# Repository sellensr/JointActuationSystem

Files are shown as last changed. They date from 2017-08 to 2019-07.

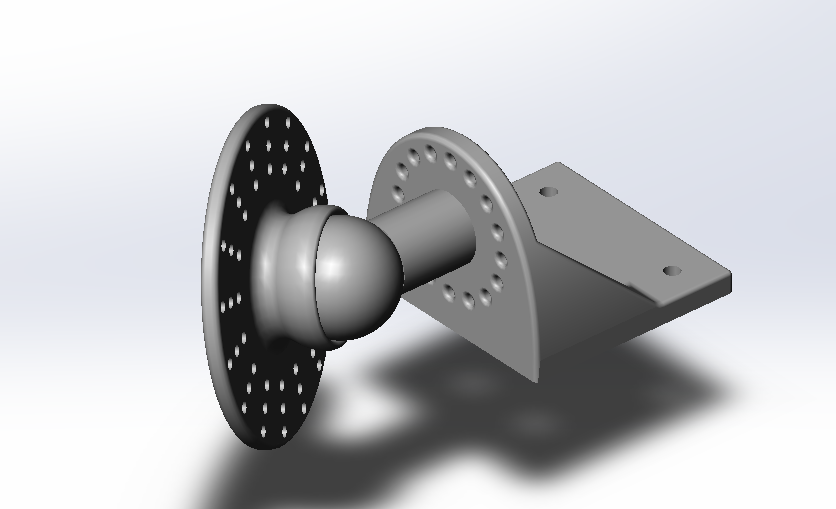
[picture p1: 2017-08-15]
Part Designs/CTP/CTP Assembly.png

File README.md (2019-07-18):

# JointActuationSystem
Details of the design of an Actuation System for wrist motion simulation as detailed in the master's thesis by Matthew Pearson titled: An Open-Source Device for Tendon Actuated Wrist Motion. 

Further details on the design, manufacture and testing are presented in the thesis found in this repository or [THESIS LINK]

Code original to the thesis is left intact in /Code/AP Source Code and /Code/Aurora AMP Source Code. Current development is taking place in /Code/MP-Sim_AP and Qualisys_AMP

## Generalization for other joints

Original coordinates and angle naming (only two angles, flexion-extension and radial-ulnar) were specific to a system of 4 actuators and the wrist joint. Additions to the /Code structure generalize to 3 x-y-z angles within a right hand coordinate system with y positive distally and z positive vertically upwards. Rotation about the x axis thus corresponds to flexion-extension and rotation about the z axis to radial-ulnar deviation in the original work on the wrist. 

Note that the original was coded to run on an Arduino Due, while the newer code is directed to hardware based on the Teensy 3.5. In addition to the Arduino IDE, you will need to download and installed the teensyduino support libraries.

https://www.pjrc.com/teensy/td_download.html

2019-04-26: Newer code for MP-Sim starts with an alpha version deceptively labelled as v2.0 to distinguish it from the original work by Matt Pearson. It is purely developmental for the moment.

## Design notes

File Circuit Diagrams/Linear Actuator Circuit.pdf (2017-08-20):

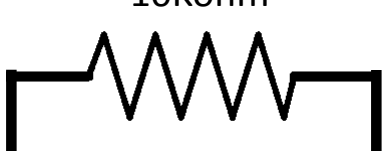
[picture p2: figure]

Yellow | White
Blue

10Kohm

Actuator

Black | Red

Red – 12V
Black - Ground

White/Yellow – Potentiometer Reference Blue – Potentiometer Wiper (Position Signal)

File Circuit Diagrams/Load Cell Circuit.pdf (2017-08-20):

5V

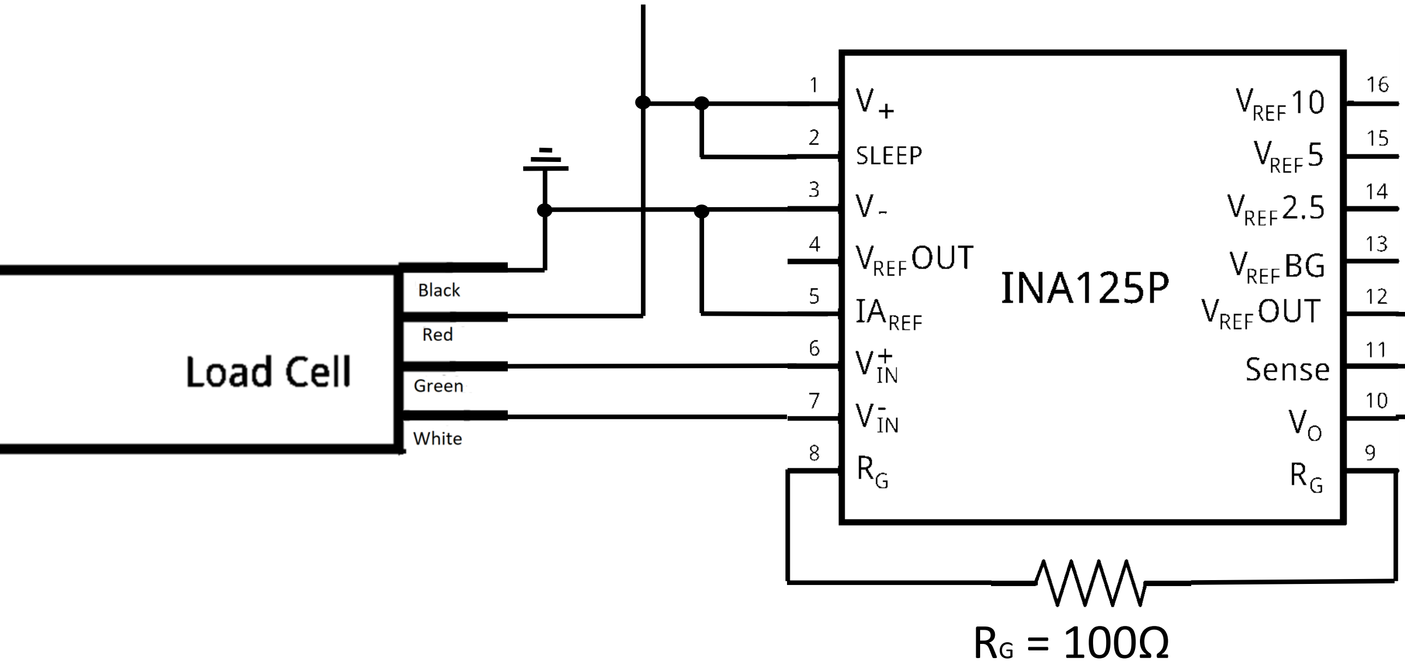
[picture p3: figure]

Voutput

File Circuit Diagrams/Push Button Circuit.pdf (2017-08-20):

Vout1 | Vout2 | Vout3 | Vout4 | Vout5

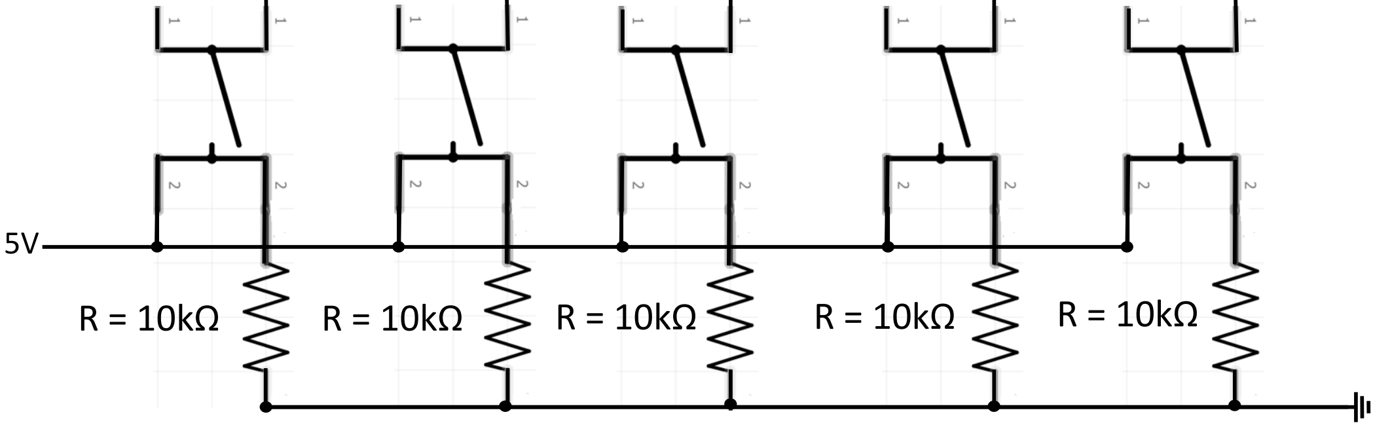
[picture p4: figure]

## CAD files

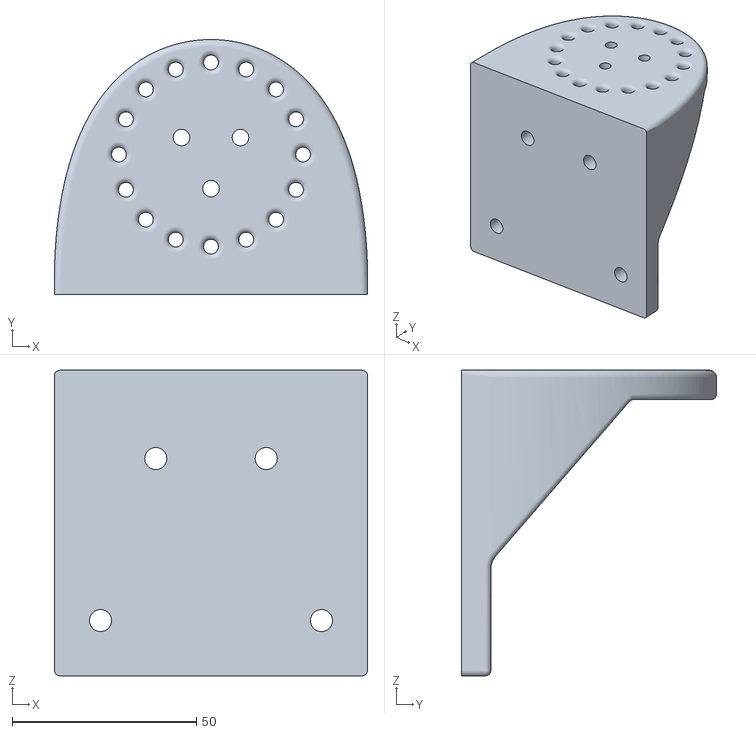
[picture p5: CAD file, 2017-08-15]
Part Designs/CTP/CTP STL Files/CTP_Base.STL
85.0 x 69.3 x 83.0

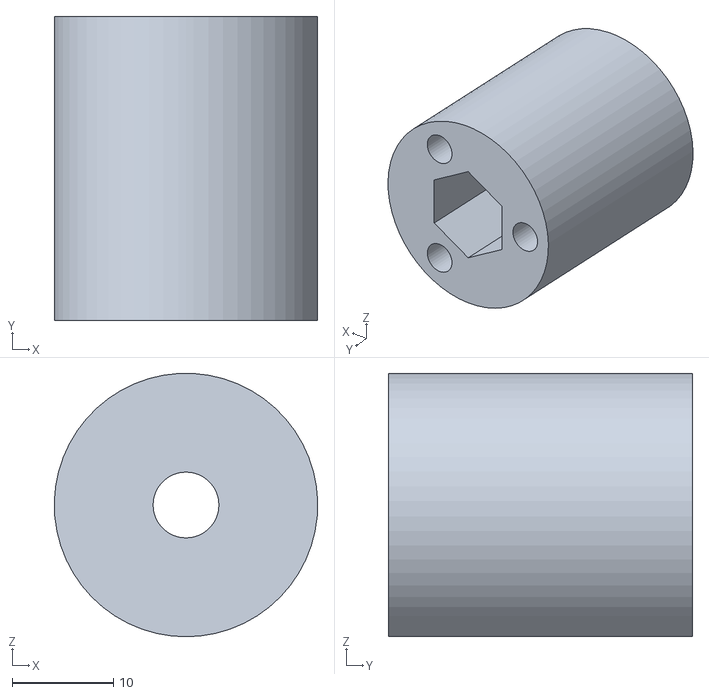
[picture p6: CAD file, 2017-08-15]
Part Designs/CTP/CTP STL Files/CTP_BallPost.STL
26.0 x 30.0 x 26.0

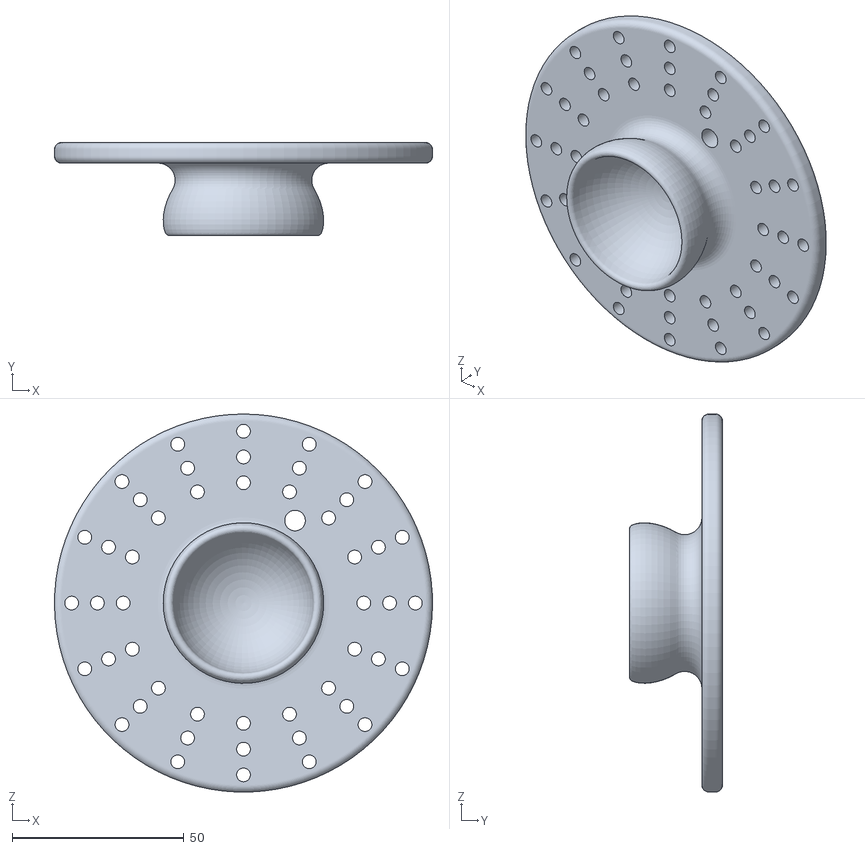
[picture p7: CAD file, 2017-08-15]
Part Designs/CTP/CTP STL Files/CTP_SocketPlatform.STL
110.0 x 27.1 x 110.0

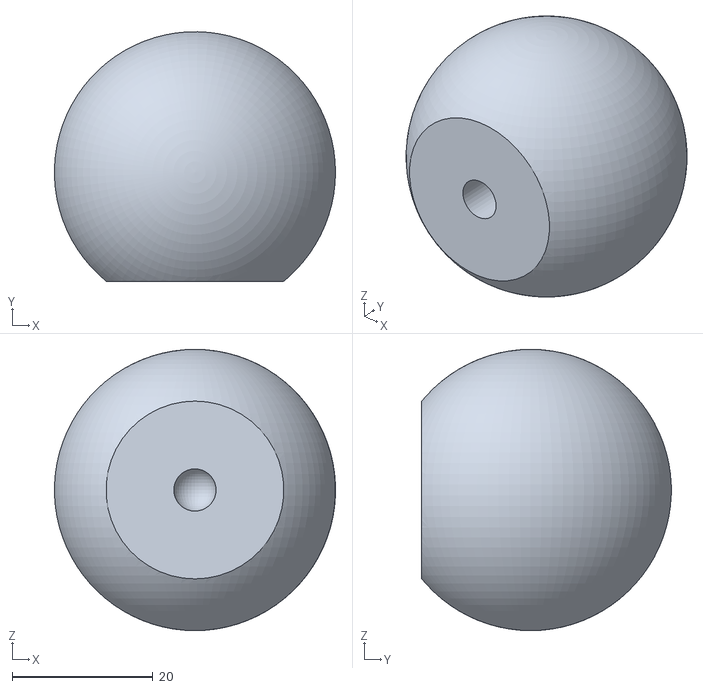
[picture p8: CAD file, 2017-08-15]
Part Designs/CTP/CTP STL Files/CTP_Ball.STL
40.0 x 35.5 x 40.0

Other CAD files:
Part Designs/AP Component Drawing and CAD/Actuator Platform Assembly/Actuator Platform Assembly.iam
Part Designs/AP Component Drawing and CAD/Actuator Platform Assembly/Load Cell.ipt
Part Designs/AP Component Drawing and CAD/CAD Part Files/Actuator Back Plate.ipt
Part Designs/AP Component Drawing and CAD/CAD Part Files/Actuator Bracket.ipt
Part Designs/AP Component Drawing and CAD/CAD Part Files/Actuator Piston Support Plate.ipt
Part Designs/AP Component Drawing and CAD/CAD Part Files/Actuator Platform Frame.ipt

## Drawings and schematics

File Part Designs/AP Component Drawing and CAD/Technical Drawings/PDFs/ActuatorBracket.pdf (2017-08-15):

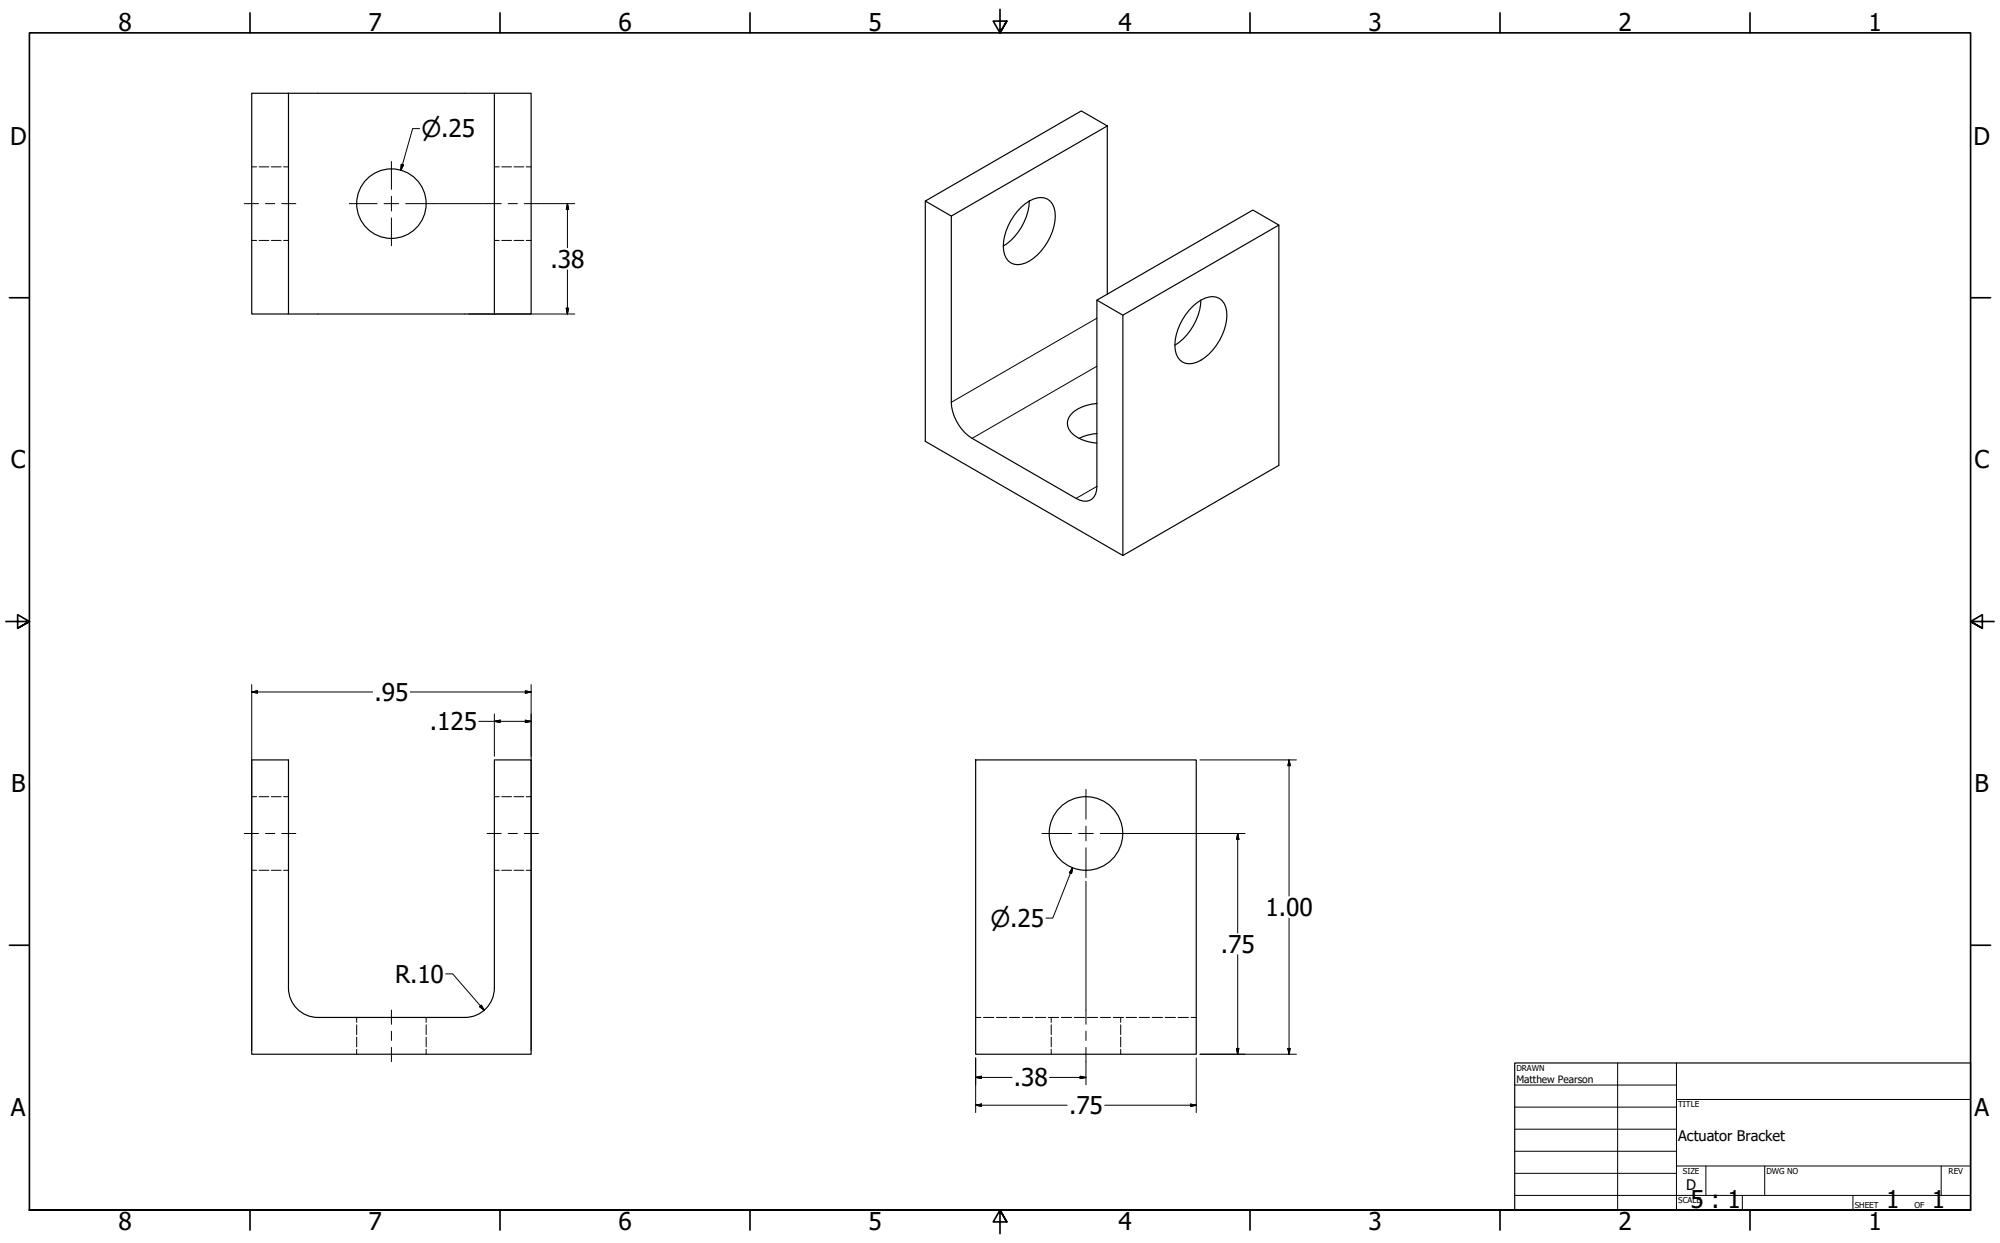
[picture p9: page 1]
Matthew Pearson; Actuator Bracket

SIZE D | DWG NO | REV

5 : 1 SCALE | | SHEET 1 OF 1

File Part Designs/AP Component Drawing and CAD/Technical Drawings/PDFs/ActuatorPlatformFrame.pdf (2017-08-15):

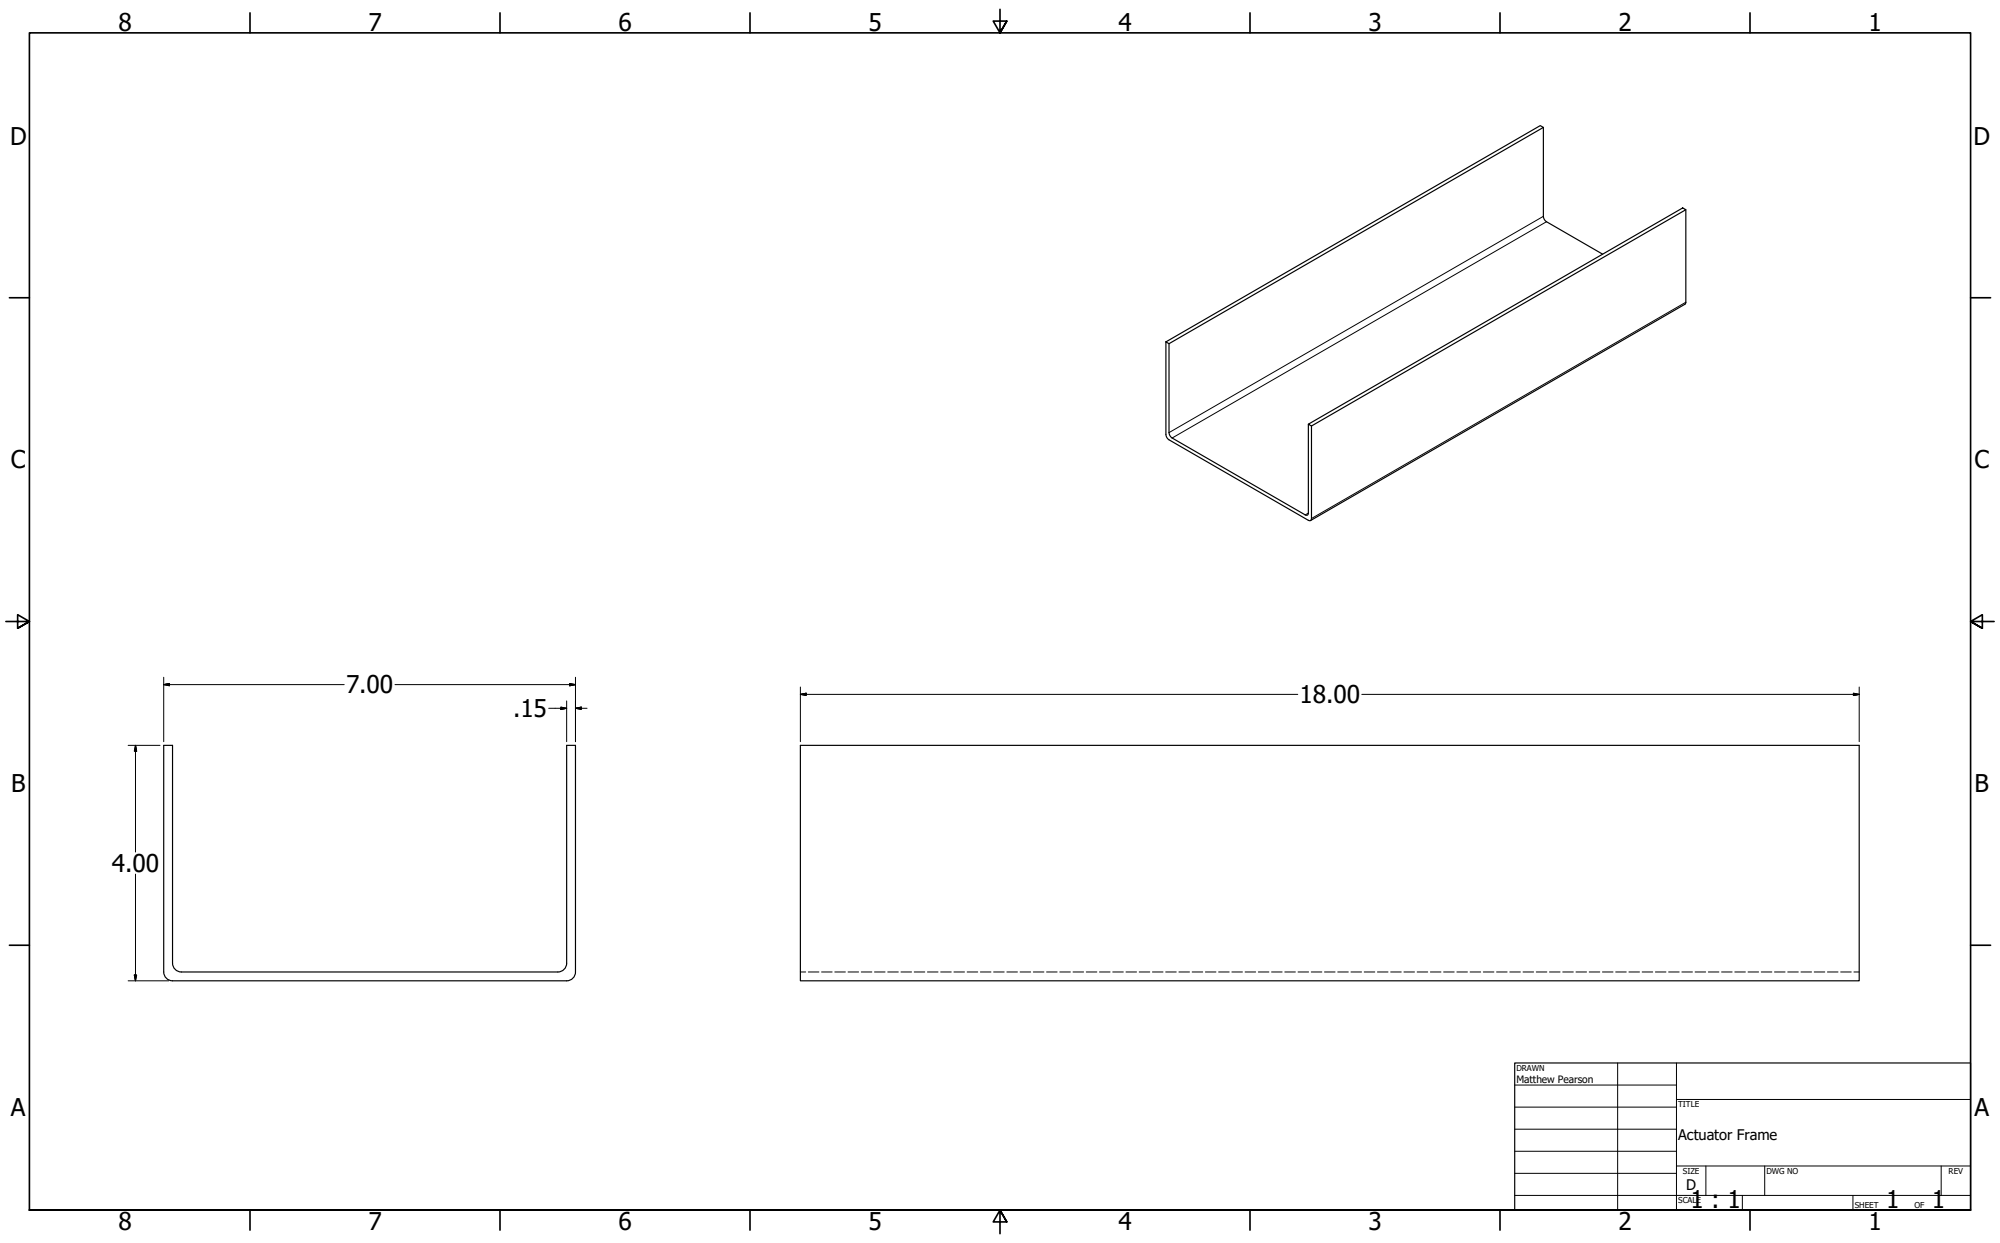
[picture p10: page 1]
Matthew Pearson; Actuator Frame

SIZE D | DWG NO | REV

1 : 1 SCALE | | SHEET 1 OF 1

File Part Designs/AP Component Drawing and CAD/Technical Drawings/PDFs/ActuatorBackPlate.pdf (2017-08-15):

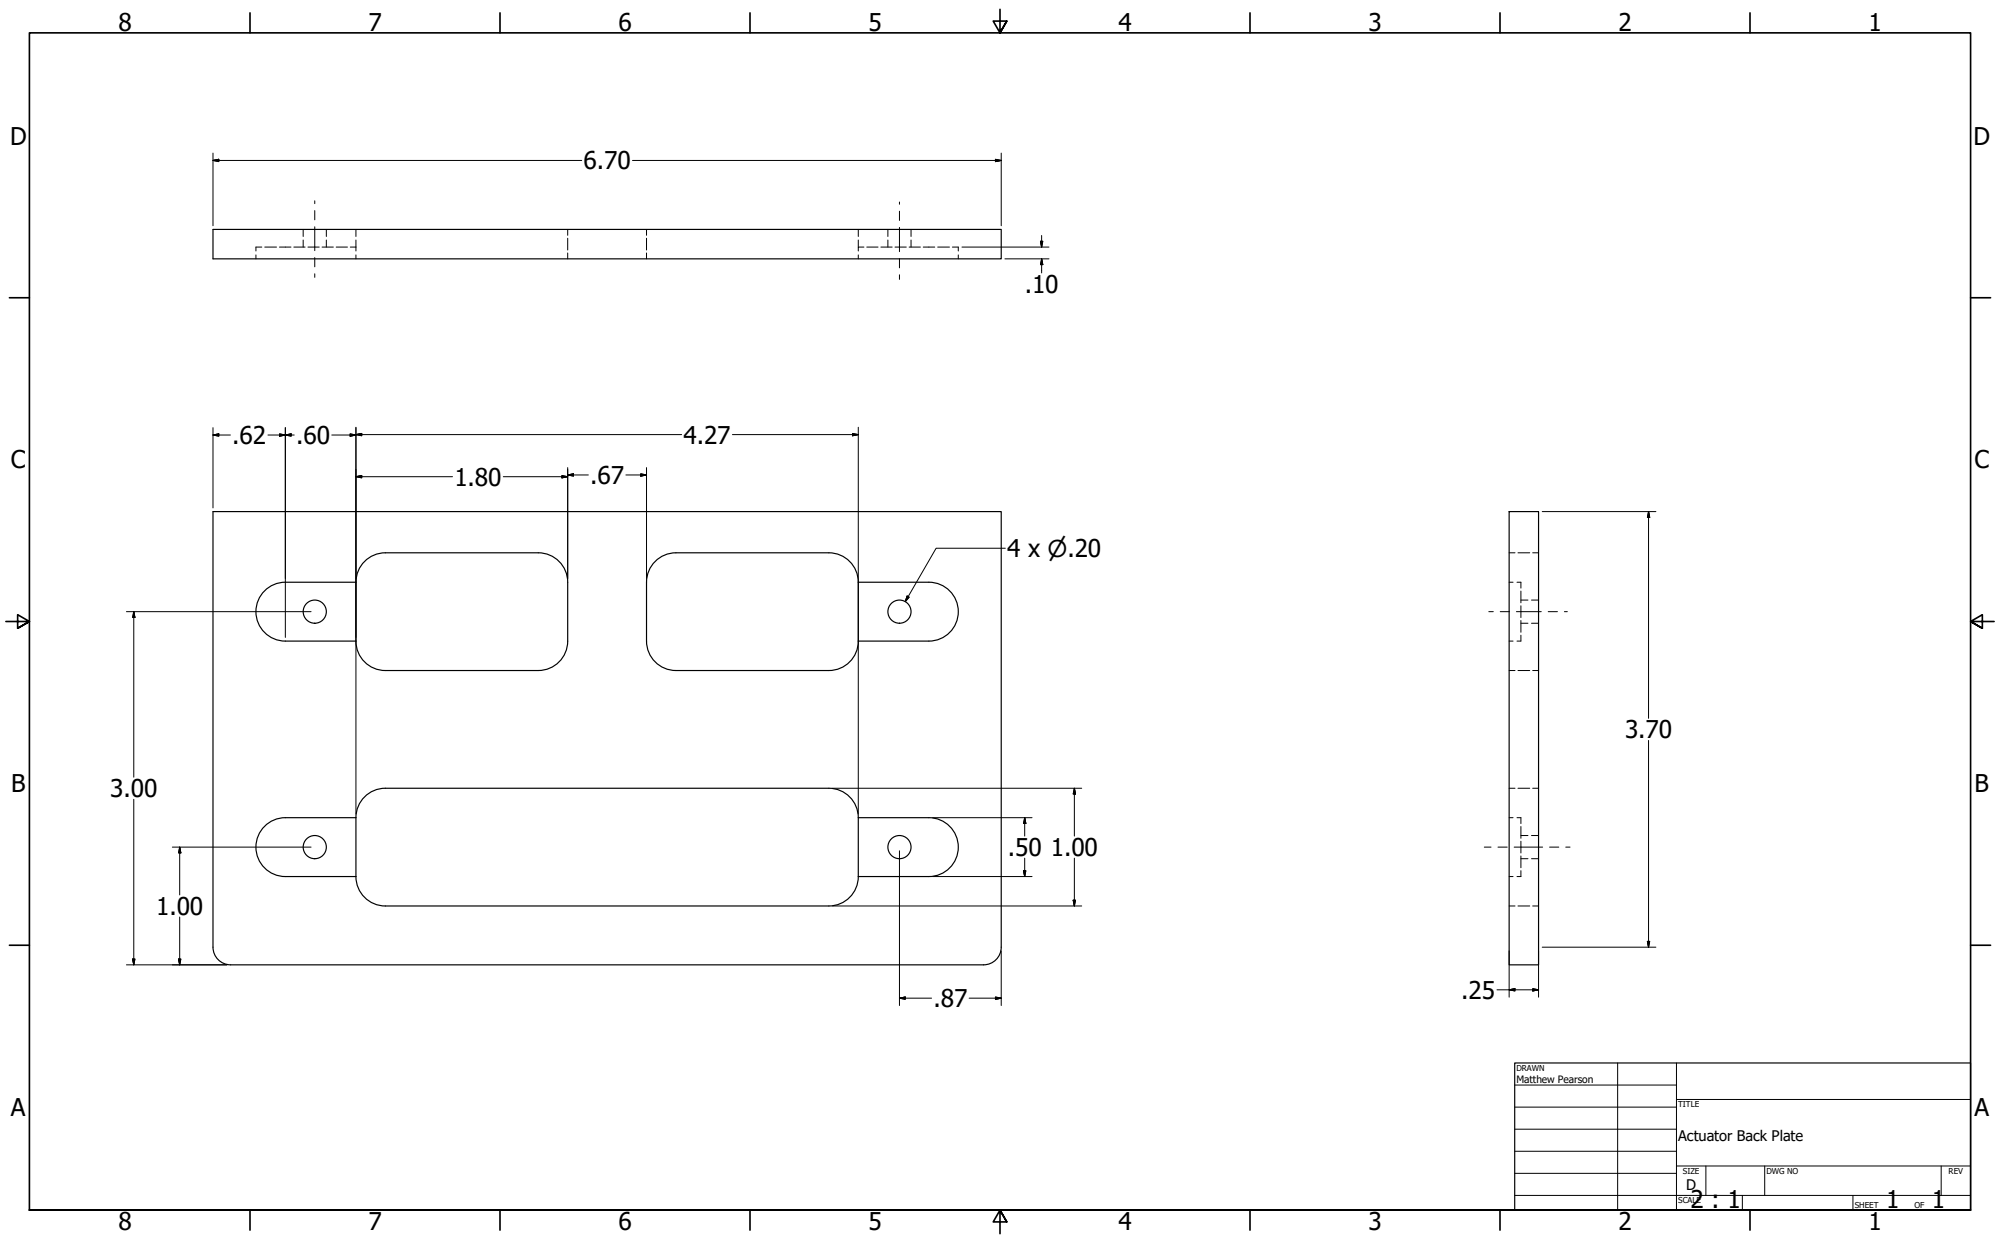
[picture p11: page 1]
Matthew Pearson

Actuator Back Plate

SIZE D | DWG NO | REV

2 : 1 SCALE | | SHEET 1 OF 1

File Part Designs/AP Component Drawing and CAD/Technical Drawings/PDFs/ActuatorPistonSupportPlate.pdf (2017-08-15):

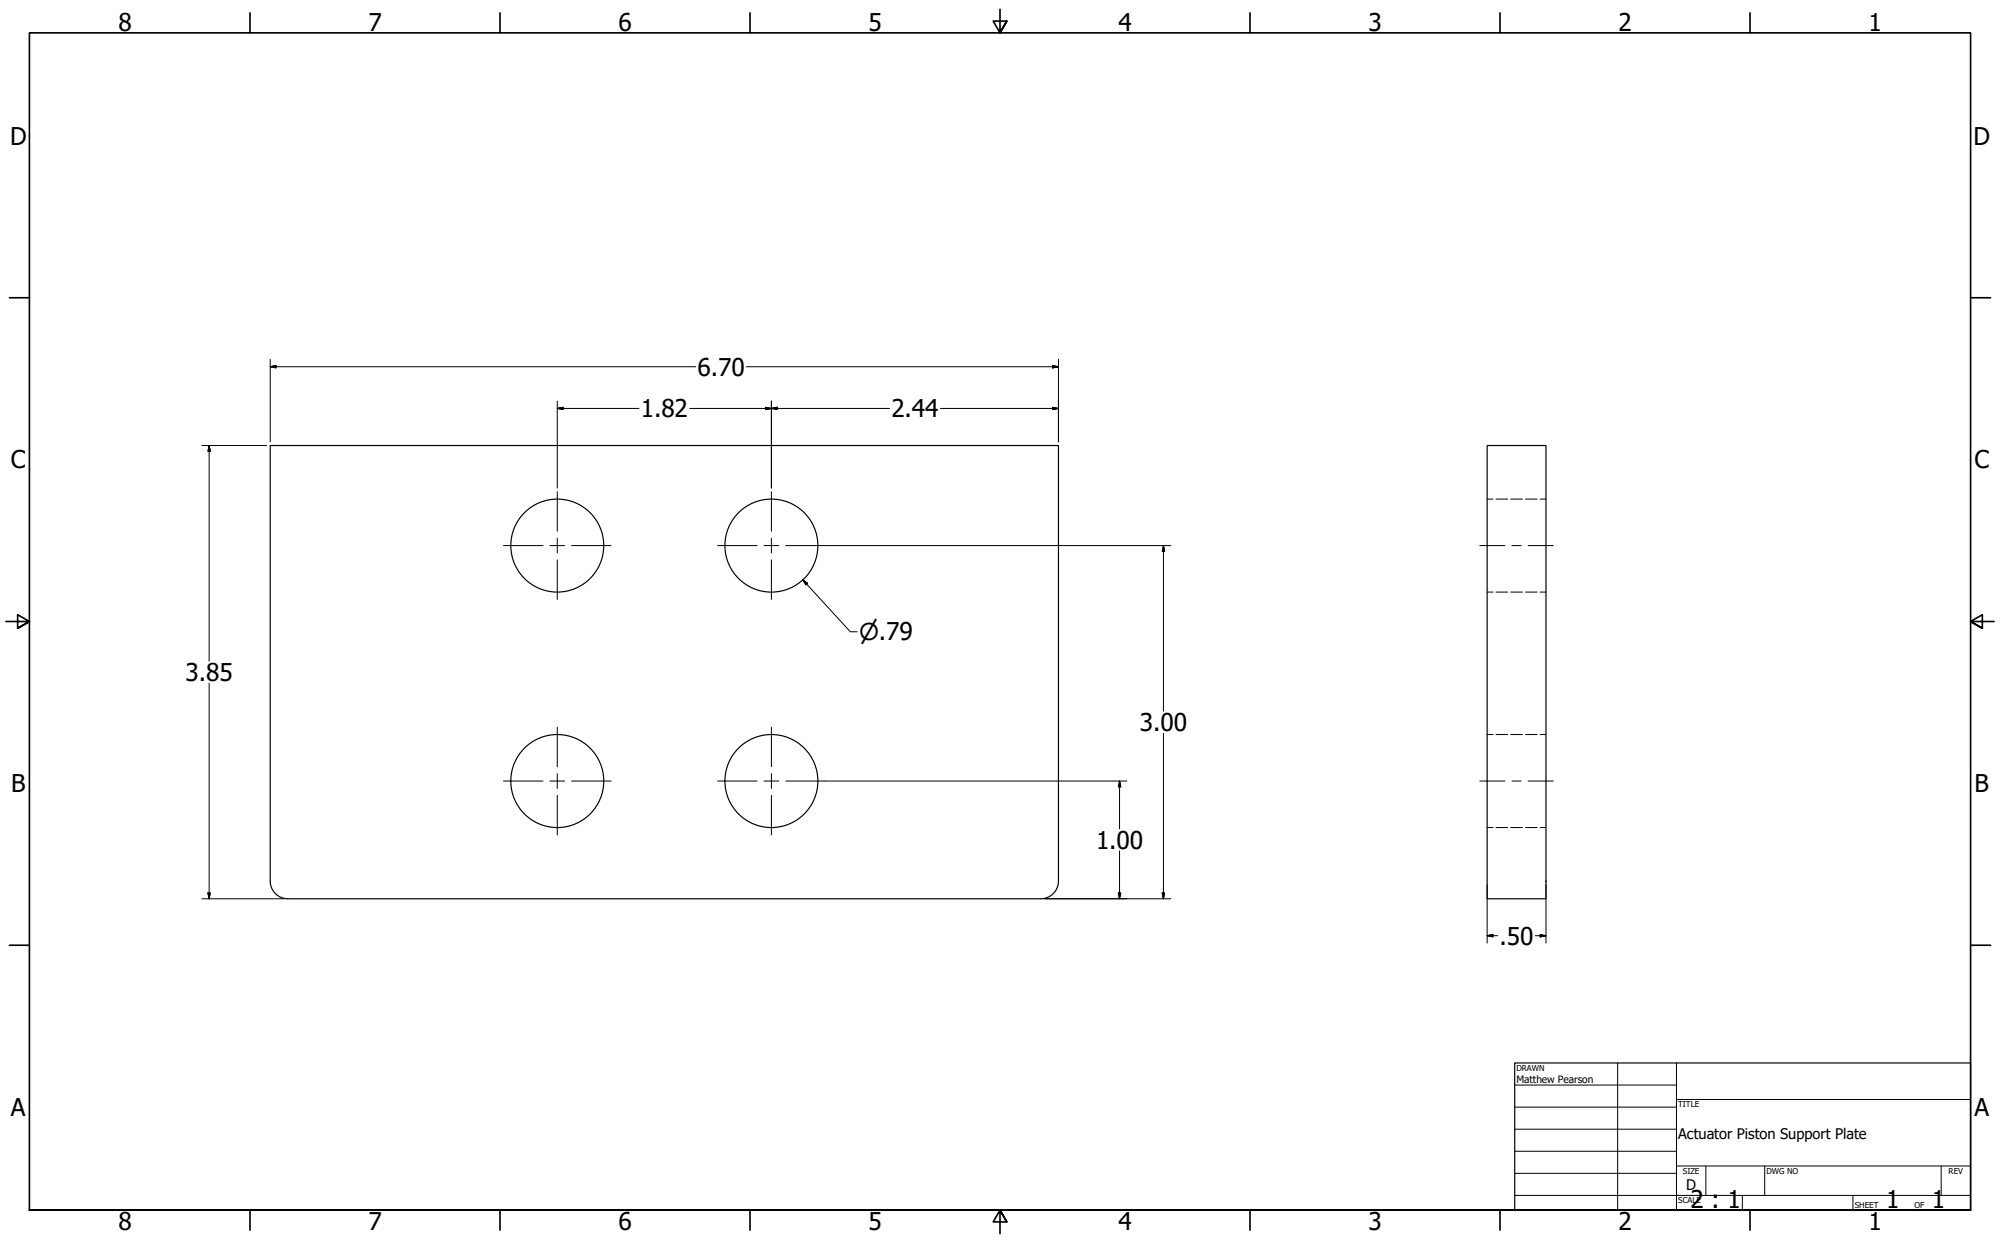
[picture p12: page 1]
Matthew Pearson

Actuator Piston Support Plate

SIZE D | DWG NO | REV

2 : 1 SCALE | | SHEET 1 OF 1

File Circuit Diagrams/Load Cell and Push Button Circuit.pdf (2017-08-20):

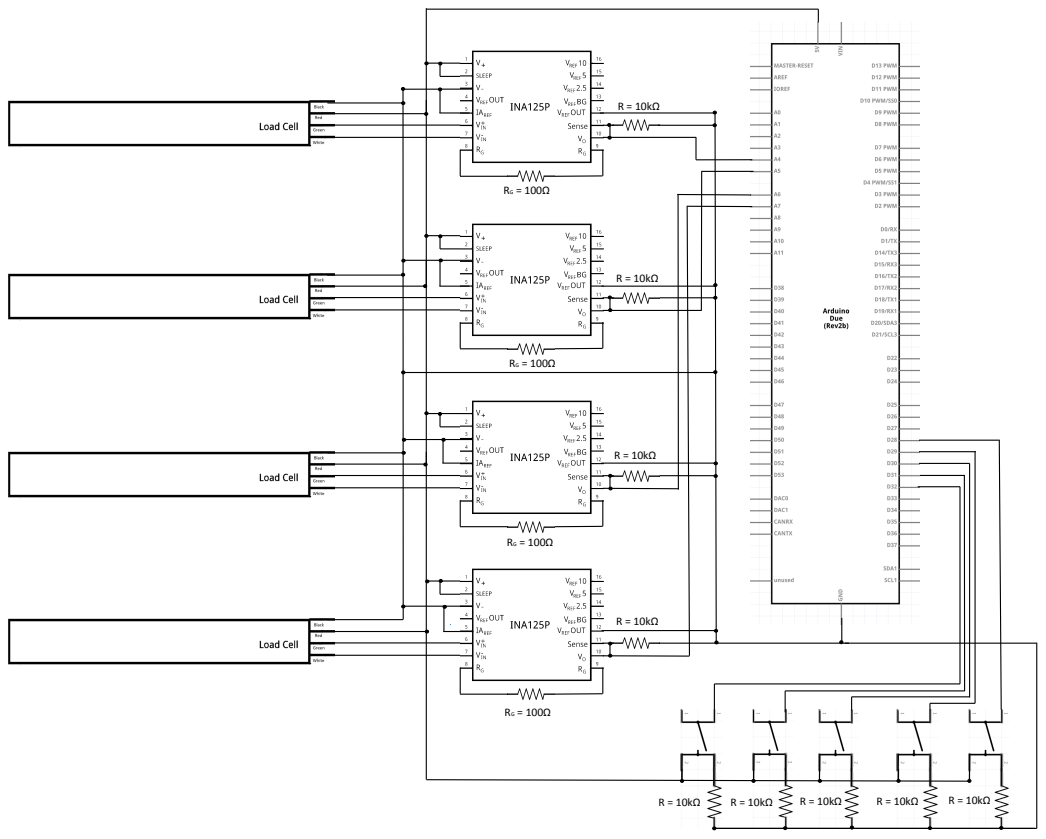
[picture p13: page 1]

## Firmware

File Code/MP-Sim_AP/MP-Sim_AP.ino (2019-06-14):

/* To Do:
 *  pushing the button should kill the gesture, 
 *  there should be a log file for CSV data
 *  the power supply sometimes trips out -- can we get a better supply or reduce current demand?
 *  rationalize location of global variables
 */



// Get tasks to fail after timing out -- motor tensioning for example
//    tensioning, extending, retracting done

// AP_ControlSystemCode V 2
#define VER            2.0
#define NCHIND         8      // make the arrays big enough we could go to 8 actuators
#define DEBUG          2      // determine how much monitoring goes to the console
#define START_TENSION  7      // starting tendon tension [N], Matt had 15
#define INC_TENSION    2      // small increase in tension [N], Matt had 5
#define MAX_TENSION   40      // maximum tension [N] to allow in any tendon, 20 too low
#define STOP_LOAD     30      // stop the motors pushing/pulling against this high a load [N]
#define MAX_SPEED    400      // maximum speed units with Pololu motor control library
#define DEF_SPEED     85      // go slower than maximum speed by default
#define MIN_SPEED     50      // minimum speed that is still actually reliably moving

#define tarMask       0b00000001
#define actMask       0b00000010
#define posMask       0b00000100
#define deltaMask     0b00001000
#define frcMask       0b00010000
#define verboseMask   0b10000000


// pick one and only one to establish AP hardware module
//#include "ch4due.h"   // obsolete now that DUE serial connector failed 2019-01-24
#include "ch6teensy.h"

/* Code for control of Actuator Platform (AP) of simulator system.
 * Receives serial input from the Angular Measurement Platform (AMP) via the Angle Interface Device (AID)
 * 
 * AP Coordinate Systems, etc. Viewed from behind the actuators
 * 
 * 
 *    z      4     5         NC    NC  
 *    ^      2     3          2     3
 *    |      0     1          0     1
 *    |   Actuator Motor    Actuator Motor 
 *    |    Numbers V2      Numbers Original
 *    |     
 *     ----------> x
 *     y is positive away from the viewer in normal RHS format
 *     Angles in degrees are arrays of 3 elements [a,b,c] corresponding to x,y,z axes.
 *      a is the x angle, 0 aligned with x-y plane, positive upwards
 *      b is the y angle, 0 aligned with x-y plane, positive clockwise
 *      c is the z angle, 0 aligned with y-z plane, positive leftwards
 *     
 *     For a right arm, palm down neutral:
 *      a is flexion-extension with extension positive
 *      b is pronation-suppination with zero pronated, increasing angle clockwise to suppination
 *        (ignored at present, but included in the angle definition for completeness)
 *      c is radial-ulnar deviation, radial deviation positive
 *      
 *      Motor speeds and positions are positive in the positive y direction, 
 *      away from the viewer, releasing tension on the tendons. 
 *      
 *      Forces should probably be negative in tension, but aren't yet
 *      
 *      Positions are in mm, positive in the positive y directionand always greater than zero.
 *      Position of 60 mm is almost fully retracted on original 4 motor rig.
 *     
 */
float posSmooth = 0.995; //closer to 0 for a fast response and closer to 1 for a smoother response
float forceSmooth = 0.99;
float posTau = 0.01;      // time constants in seconds 2019-02-22
float forceTau = 0.01;

//global variables for functions
int motorEnabled[NCHIND]   = {1, 1, 1, 1, 0, 0, 0, 0};   // set to zero for motors not to be used
float motorGoalPos[NCHIND] = {0, 0, 0, 0, 0, 0, 0, 0};   // mm
//variables for smoothing Pos and force
double oldPos[NCHIND] = {0, 0, 0, 0, 0, 0};              // most recent smoothed position data [mm]
double latestPos[NCHIND] = {0, 0, 0, 0, 0, 0};           // most recently read position data [mm]   
double inPos[NCHIND] = {70, 70, 70, 70, 70, 70};         // fully retracted motor positions [mm]
double midPos[NCHIND] = {100, 100, 100, 100, 100, 100};  // mid range motor positions [mm]
double outPos[NCHIND] = {140, 140, 140, 140, 140, 140};  // fully extended motor positions [mm]
float oldForce[NCHIND] = {0, 0, 0, 0, 0, 0};             // most recent smoothed force data [N]
float latestForce[NCHIND] = {0, 0, 0, 0, 0, 0};          // most recently read force data [N]
float deltaPos[NCHIND] = {0, 0, 0, 0, 0, 0};             // desired change in position [mm]

//Second Arduino Program Tab

float gBase = 0.04;         // scaled gain values all positive [mm / degree / iteration]
float range = 0.5 * gBase;  // choose what to do "range" is angle tolerance * gain

// Treating pulling on the tendons as a negative position actuation, gain is negative 
// if pulling on that tendon would increase the angle. The gain is in units of 
// position change desired to increase a given angle [mm / degree / iteration]. 
// angle[0] is increased by pulling on actuators 2 and 3 of the 4CH system
                             // and probably 4 5 as well in the 6CH system
// angle[0] is decreased by pulling on actuators 0 and 1 of the 4CH system
float gains[3][NCHIND] = {  { gBase,  gBase, -gBase, -gBase, -gBase, -gBase},      
                            // angle[1] is about the y axis and we don't care yet
                            {     0,      0,      0,      0,      0,      0},  
                            // angle[3] is increased by pulling on the left (0,2,4)    
                            {-gBase,  gBase, -gBase,  gBase, -gBase,  gBase} };    
  

// Note that v1.0 angles are different and wrist oriented, with pronation/supination ignored.
// Qualisys angle measurement version will deliver x angle, y angle, z angle in hundredths of a degree
// Floating point angles are in degrees.
//     float wristAng[3] = {0, 0, 0}; //latest position of the wrist {RUD, FE, PS}
float actAng[3] = {0, 0, 0};   //latest position in actuator coordinates {x axis angle,y axis angle,z axis angle}
float tarAng[3] = {0, 0, 0};   //current target angle in actuator coordinates {x axis angle,y axis angle,z axis angle}
float neutAng[3] = {0, 0, 0};   //neutral target angle in actuator coordinates {x axis angle,y axis angle,z axis angle}
float deltaAng[3] = {0, 0, 0}; //target angle - current angle
// conversion factors from analog read units to mm of position
float mmPerUnit[NCHIND] = {0.003009598, 0.003009598, 0.003009598, 0.003009598, 0.003009598, 0.003009598};


/////Initialize all pinModes and TIMER 1, set PWN to 20kHZ--------------------------------------------------------------
void initializePins(){
  for(int x = 0; x < NCH; x++){
    pinMode(_INA[x],OUTPUT);
    pinMode(_INB[x],OUTPUT);
    pinMode(_PWM[x],OUTPUT);
    pinMode(_ENGDIAG[x],INPUT);
    pinMode(_CS[x],INPUT);
  }  

  // 5 buttons on the 4CHDUE version and button #4 is the big red one
  for(int x = 0; x < 5; x++) pinMode(buttonPin[x], INPUT);  
}

//  Short function to check if a button is pressed or not for 0 to 4
//  Not used for anything in the original, except buttonStatus(4)
// Pulled low normally, connected to high when pushed
unsigned int buttonStatus(int button){
  return digitalRead(buttonPin[button]);
}


//Function to initialize the smoothed actuator position for all actuators---------------------------------------------------------
//To correct and for the delayed smoothed readings, position readings must be taken many times
//This function is meant for the setup{} of the main code and prints out each motors current position
void initializePosition(){
  Serial.print("Initial Motor Position Readings:");
  for(int j = 0;j<1000;j++) for(int i = 0; i < NCH; i++) smoothMotorPos(i);
  for(int i = 0; i < NCH; i++){
    Serial.print("  "); Serial.print(smoothMotorPos(i));
  }
  Serial.print("\n");
}

void updateMotorPos(){ for(int i = 0;i<NCH;i++) smoothMotorPos(i);}

///// Return Smoothed Analog Read Position of motor Calibrated into MILLIMETERS--------------------------------------------
double smoothMotorPos(int motor){
  static unsigned long timeLastP[NCHIND] = {0};
  unsigned long timeNowP = micros();
  float dt = (timeNowP-timeLastP[motor])/1000000.;
  if(dt > posTau) posSmooth = 0;
  else posSmooth = 1-dt/posTau;
  latestPos[motor] = analogRead(_POS[motor]) * mmPerUnit[motor];
  oldPos[motor] = posSmooth * oldPos[motor] + (1 - posSmooth) * latestPos[motor];
  return oldPos[motor];
}

//Initilizing the smoothed force readings, this is the same as for position measurements--------------------------------
void initializeForce(){
  // set grams / analogRead unit based on input values 1 lb = 454 g
  for(int i = 0;i < NCH;i++) _FRCMULTI[i] = 4540. / (_LB10OFFSET[i] - _GRAVOFFSET[i]);
  Serial.print("   Initial Motor Force Readings:");
  for(int j=0;j<1000;j++) for(int i = 0; i < NCH; i++) smoothForce(i);
  for(int i = 0; i < NCH; i++){
    Serial.print("  ");
    Serial.print(smoothForce(i));
  }
  Serial.print("\n");
}

void updateForce(){ for(int i = 0;i<NCH;i++) smoothForce(i);}

/////Return Smoothed Calibrated analog read of force of motor IN NEWTONS-------------------------------------------------------
float smoothForce(int motorF){
  static float NperGram =  .00980665002864; // N per g under 1g field = 9.8 N per kg
  static unsigned long timeLastF[NCHIND] = {0};
  unsigned long timeNowF = micros();
  float A = analogRead(_FRC[motorF]);
  float dt = (timeNowF-timeLastF[motorF])/1000000.;
  if(dt > forceTau) forceSmooth = 0;
  else forceSmooth = 1-dt/forceTau;
  latestForce[motorF] = NperGram * ((A - _FRCOFFSET[motorF] ) * _FRCMULTI[motorF]); // Newtons
  oldForce[motorF] = (forceSmooth * oldForce[motorF] + (1 - forceSmooth) * latestForce[motorF]);
  timeLastF[motorF] = timeNowF;
  return oldForce[motorF]; 
}

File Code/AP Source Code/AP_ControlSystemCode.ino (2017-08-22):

//First Arduino Program Tab
//Array created using Excel and copied into the code
//5rad 10flex shifted left 5 this is fully ulnar clockwise circumduction
float array[] = {-5,10,-4.686047402,9.980267284,-4.373333832,9.921147013,-4.063093427,9.822872507,-3.756550564,9.685831611,
-3.454915028,9.510565163,-3.159377237,9.297764859,-2.871103542,9.048270525,-2.591231629,8.7630668,-2.320866025,8.443279255,
-2.061073739,8.090169944,-1.812880051,7.705132428,-1.57726447,7.289686274,-1.355156863,6.845471059,-1.147433786,6.374239897,
-0.954915028,5.877852523,-0.778360372,5.35826795,-0.6184666,4.817536741,-0.475864738,4.257792916,-0.351117571,3.681245527,
-0.244717419,3.090169944,-0.157084194,2.486898872,-0.088563746,1.873813146,-0.039426493,1.253332336,-0.009866358,0.627905195,
0,-6.04876E-15,-0.009866358,-0.627905195,-0.039426493,-1.253332336,-0.088563746,-1.873813146,-0.157084194,-2.486898872,
-0.244717419,-3.090169944,-0.351117571,-3.681245527,-0.475864738,-4.257792916,-0.6184666,-4.817536741,-0.778360372,-5.35826795,
-0.954915028,-5.877852523,-1.147433786,-6.374239897,-1.355156863,-6.845471059,-1.57726447,-7.289686274,-1.812880051,-7.705132428,
-2.061073739,-8.090169944,-2.320866025,-8.443279255,-2.591231629,-8.7630668,-2.871103542,-9.048270525,-3.159377237,-9.297764859,
-3.454915028,-9.510565163,-3.756550564,-9.685831611,-4.063093427,-9.822872507,-4.373333832,-9.921147013,-4.686047402,-9.980267284,
-5,-10,-5.313952598,-9.980267284,-5.626666168,-9.921147013,-5.936906573,-9.822872507,-6.243449436,-9.685831611,-6.545084972,
-9.510565163,-6.840622763,-9.297764859,-7.128896458,-9.048270525,-7.408768371,-8.7630668,-7.679133975,-8.443279255,-7.938926261,
-8.090169944,-8.187119949,-7.705132428,-8.42273553,-7.289686274,-8.644843137,-6.845471059,-8.852566214,-6.374239897,-9.045084972,
-5.877852523,-9.221639628,-5.35826795,-9.3815334,-4.817536741,-9.524135262,-4.257792916,-9.648882429,-3.681245527,-9.755282581,
-3.090169944,-9.842915806,-2.486898872,-9.911436254,-1.873813146,-9.960573507,-1.253332336,-9.990133642,-0.627905195,-10,
-1.83772E-15,-9.990133642,0.627905195,-9.960573507,1.253332336,-9.911436254,1.873813146,-9.842915806,2.486898872,-9.755282581,
3.090169944,-9.648882429,3.681245527,-9.524135262,4.257792916,-9.3815334,4.817536741,-9.221639628,5.35826795,-9.045084972,
5.877852523,-8.852566214,6.374239897,-8.644843137,6.845471059,-8.42273553,7.289686274,-8.187119949,7.705132428,-7.938926261,
8.090169944,-7.679133975,8.443279255,-7.408768371,8.7630668,-7.128896458,9.048270525,-6.840622763,9.297764859,-6.545084972,
9.510565163,-6.243449436,9.685831611,-5.936906573,9.822872507,-5.626666168,9.921147013,-5.313952598,9.980267284,-5,10};
int iN = 0; //counter for arrays

//the following are declarations for each variable
//pins for each variable in array form, call motors 0 to 3 with [0],[1],[2],[3]
unsigned char _INA[] = {2, 7, 22, 25};
unsigned char _INB[] = {4, 8, 23, 3};
static const unsigned char _PWM[] = {9, 10, 5, 13};
unsigned char _ENGDIAG[] = {6, 12, 24, 11};
unsigned char _CS[] = {A0, A1, A2, A3};
unsigned char _POS[] = {A8, A10, A9, A11};
unsigned char _FRC[] = {A4, A5, A6, A7};
const int buttonPin[] = {28, 29, 30, 31, 32}; //pins for the added push buttons
//end pin declaration--------------------------------------------------------------------------------------

//Calibration variables constants 
unsigned int _FRCOFFSET[] = {4607, 3345, 2665, 5805};
double _FRCMULTI[] = {0.3323, 0.3308, 0.3318, 0.3198};
double _POSOFFSET[] = {3.00959, 0, 0, 0};
float posSmooth = 0.995; ////closer to 0 for a fast response and closer to 1 for a smoother response
float forceSmooth = 0.99;

//global variables for functions
float motorGoalPos[] = {0, 0, 0, 0};
//variables for smoothing Pos and force
double oldPos[] = {0, 0, 0, 0};
float oldForce[] = {0, 0, 0, 0};
float oldAnalogForce[] = {0, 0, 0, 0};
float mtrForce = 0;
float mtrAnalogForce = 0;
double mtrPos = 0;


#define STARTTENSION 15

long ruda, fea;      //vars for anglular positions for getAngles
float rudaF, feaF;

/////Initialize all pinModes and TIMER 1, set PWN to 20kHZ--------------------------------------------------------------
void initialize(){
  for(int x = 0; x < 4; x++){
    pinMode(_INA[x],OUTPUT);
    pinMode(_INB[x],OUTPUT);
    pinMode(_PWM[x],OUTPUT);
    pinMode(_ENGDIAG[x],INPUT);
    pinMode(_CS[x],INPUT);
  }  
  
  for(int x = 0; x < 5; x++){
    pinMode(buttonPin[x], INPUT);
  }
  
  #if defined(__AVR_ATmega168__)|| defined(__AVR_ATmega328P__)//this is not for the DUE
  // Timer 1 configuration
  // prescaler: clockI/O / 1
  // outputs enabled
  // phase-correct PWM
  // top of 400
  //
  // PWM frequency calculation
  // 16MHz / 1 (prescaler) / 2 (phase-correct) / 400 (top) = 20kHz
  TCCR1A = 0b10100000;  //for 9/10
  TCCR1B = 0b00010001;  //for 9/10
  TCCR4A = 0b10100000;  //for 6/13
  TCCR4B = 0b00010001;  //for 6/13
  TCCR3A = 0b10100000;  //for 5
  TCCR3B = 0b00010001;  //for 5
  ICR1 = 400;
  #endif
}

//Short function to check if a button is pressed or not for 0 to 4
unsigned int btnStatus(int button){
  return digitalRead(buttonPin[button]);
}
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

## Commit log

2019-06-07 Made Tensioning timeout user controlled
    extended period of tensioning can be used to watch agle outputs, etc. as you move the joint
2020-01-05 Rev 1 Hardware Changes
    Moved pins around to make connection wiring easier
